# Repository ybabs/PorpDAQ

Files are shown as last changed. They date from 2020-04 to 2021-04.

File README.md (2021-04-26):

# PorpDAQ
STM32 Based design data acquisition recorder for harbour porpoises. The system is based on a 40dB bandpass preamplifier (90Khz - 150kHz). Records WAV file at a sampling rate of 400 KHz (V1) and 500 KHz (V2) and stores them to a microSD card. The preamplifier was designed using TI's filter designer tool. Preamp output is passed to a summing amplifier to keep signals within 0 - 3.3V with a 1.65V bias. There's a few iterations of the DAQ from the initial prototypes to improved designs. 

PorpDAQ has been designed to fit within a small multirotor UAV so current design weighs only 18g. PorpDAQ computes a 1024 point RFFT of incoming hydrophone signals and transmits signals within 90 - 150KHz over a UART Interface

## Rev 1 Board                         

The initial version of the DAQ was based on a STM32F746 chip and had a 400 KHz sample rate and a 12-bit ADC with a SD card write speed of about 20mbps. 

<p align="left">
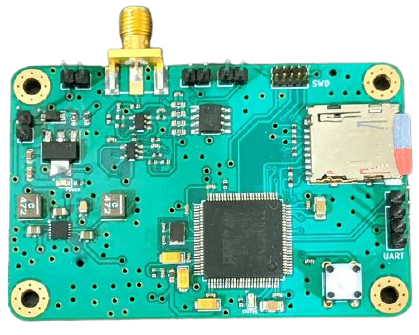
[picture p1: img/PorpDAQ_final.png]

</p>

## Rev 2 Board

Rev 2 board comes with some improvements namely the the use of the STM32H743 chip, USB-C for power with the addition of a full speed interface. 500 KHz sample rate, SD Card write speed of ~35 Mbps with a 16-bit ADC and better SNR. Also slightly smaller footprint 
<br />
<p align="left">
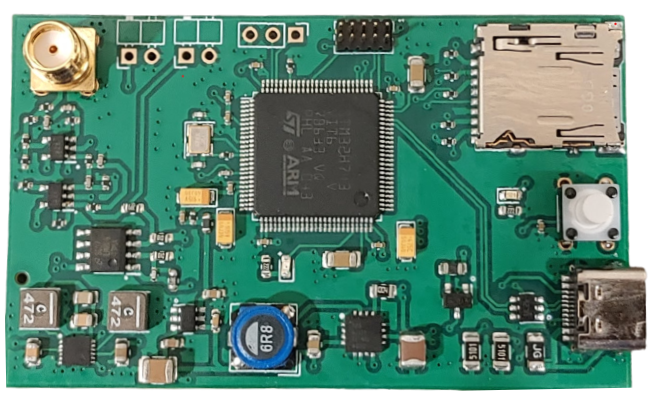
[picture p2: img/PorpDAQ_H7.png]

</p>

This repository mostly contains :
   - Hardware designs for the both revisions (circuits were simulated in MultiSim and designs were made in UltiBoard and Kicad)
   - Designs for the  different prototypes used.
   - A CM4-based design to integrate PorpDaq with a Pi4 Compute Module (WIP)
   - 3D designed case for the Rev 1 board 
   - Low level drivers and firmware (bare-metal version and FreeRTOS version for Rev1 and FreeRTOS version for Rev2)

## Note Rev2.1 now included as well.
  - 3.3V regulator on Rev 2 used a switcher and wasn't running in low noise mode (oops!) so 2.1 now uses a low noise ADP7156 3.3V regulator

## Structure
 - Firmware: Contains Custom Board FreeRTOS firmware and STM32F7 discovery board FreeRTOS and bare-metal firmware. Also contains H747 Disco Board firmware.  Please note bare-metal firmware currently has a UART TX bug preventing data from being transmmitted over the UART line.
 - Hardware: contains various designs and schematics for the board designs. **Rev 1** design is named `board_100pin` while  **Rev 2** design is named `h7_board`. 

 ## Citation (Bibtex)

` @article{Babatunde2020,
  doi = {10.3390/s20216064},
  url = {https://doi.org/10.3390/s20216064},
  year = {2020},
  month = oct,
  publisher = {{MDPI} {AG}},
  volume = {20},
  number = {21},
  pages = {6064},
  author = {Daniel Babatunde and Simon Pomeroy and Paul Lepper and Ben Clark and Rebecca Walker},
  title = {Autonomous Deployment of Underwater Acoustic Monitoring Devices Using an Unmanned Aerial Vehicle: The Flying Hydrophone},
  journal = {Sensors}
}`

## License
  MIT License Copyright 2020 Daniel Babatunde

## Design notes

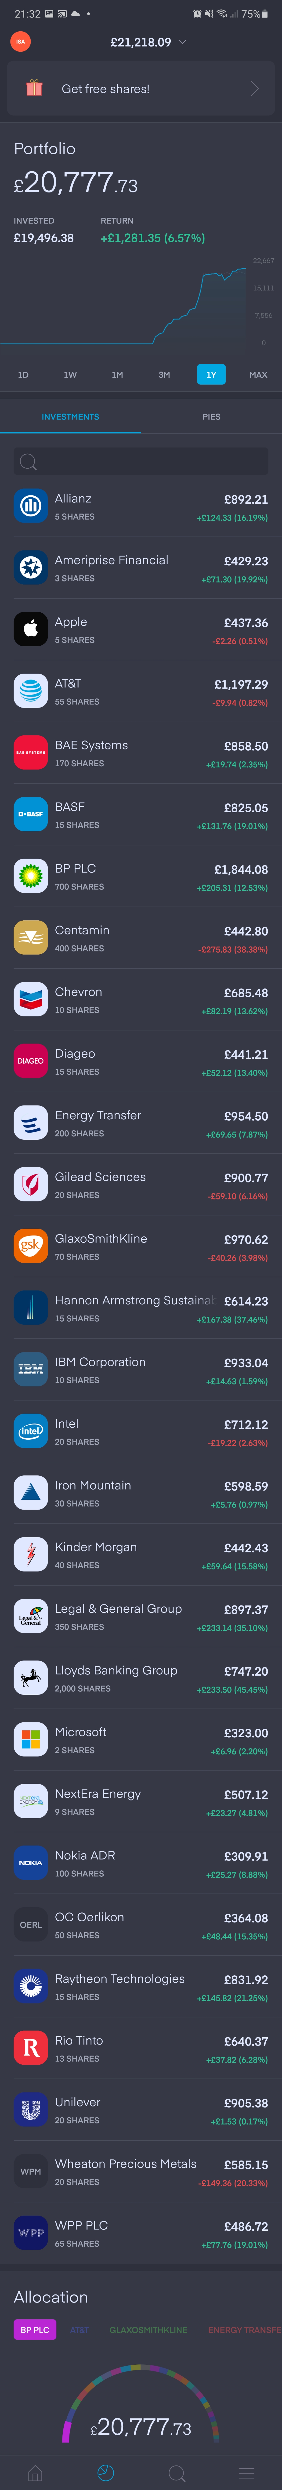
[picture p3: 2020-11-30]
Hardware/h7_lownoise/datasheets/dvi39qfev1261.jpg

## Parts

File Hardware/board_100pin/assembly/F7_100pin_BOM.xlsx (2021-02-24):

Ref | Qnty | Value | Cmp name | Footprint | Description | Manufacturer | Part Number
C2, C1, | 2 | 2.2u | C_Small | Capacitor_SMD:C_1206_3216Metric | Unpolarized capacitor, small symbol | Yageo | CC1206KKX7R7BB225 | https://www.digikey.co.uk/product-detail/en/yageo/CC1206KKX7R7BB225/311-1957-1-ND/5195859 | 0.096 | 0.192
C6, C4, C5, C3, | 4 | 100p | C_Small | Capacitor_SMD:C_0402_1005Metric | Unpolarized capacitor, small symbol | Yageo | CC0402JRNPO9BN101 | https://www.digikey.co.uk/product-detail/en/yageo/CC0402JRNPO9BN101/311-1024-1-ND/302941 | 0.0062 | 0.0248
C7, C8, | 2 | 4.3p | C_Small | Capacitor_SMD:C_0402_1005Metric | Unpolarized capacitor, small symbol | Murata | GJM1555C1H4R3BB01D | https://www.digikey.co.uk/product-detail/en/murata-electronics/GJM1555C1H4R3BB01D/490-8582-6-ND/4380999 | 0.048 | 0.096
C9, | 1 | 10p | C_Small | Capacitor_SMD:C_0402_1005Metric | Unpolarized capacitor, small symbol | Yageo | CC0402DRNPO9BN100 | https://www.digikey.co.uk/product-detail/en/yageo/CC0402DRNPO9BN100/311-3651-1-ND/8024740 | 0.0085 | 0.0085
C10, C11, | 2 | 10u | C_Small | Capacitor_SMD:C_0603_1608Metric | Unpolarized capacitor, small symbol | Murata | GRM188R61A106KE69J | https://www.digikey.co.uk/product-detail/en/murata-electronics/GRM188R61A106KE69J/490-14372-2-ND/6606001 | 0.01914 | 0.03828
C12, C13, C15, | 3 | 10u | C_Small | Capacitor_SMD:C_0805_2012Metric | Unpolarized capacitor, small symbol | Murata | GRM21BR71A106KE51 |  | 0.10981 | 0.32943
C14, | 1 | 100n | C_Small | Capacitor_SMD:C_0805_2012Metric | Unpolarized capacitor, small symbol | Murata | GRM21BR71E104KA01 |  | 0.02461 | 0.02461
C16, | 1 | 4.7u | CP_Small | Capacitor_Tantalum_SMD:CP_EIA-3216-18_Kemet-A | Polarized capacitor, small symbol | KEMET | T491A475K016AT | https://www.digikey.co.uk/product-detail/en/kemet/T491A475K016AT/399-3697-1-ND/819022 | 0.1487 | 0.1487
C24, C22, | 2 | 1u | CP_Small | Capacitor_Tantalum_SMD:CP_EIA-3216-18_Kemet-A | Polarized capacitor, small symbol | KEMET | T491A105K016AT | https://www.digikey.co.uk/product-detail/en/kemet/T491A105K016AT/399-3678-1-ND/819003 | 0.1218 | 0.2436
C26, C25, C23, C17, C18, C19, C20, C21, | 8 | 100n | C_Small | Capacitor_SMD:C_0402_1005Metric | Unpolarized capacitor, small symbol | Yageo | CC0402ZRY5V7BB104 | https://www.digikey.co.uk/product-detail/en/yageo/CC0402ZRY5V7BB104/311-1047-6-ND/578899 | 0.048 | 0.384
D1, | 1 | B5819W | D_Schottky_Small | Diode_SMD:D_SOD-123 | Schottky diode, small symbol | Micro-Commercial | B5819W-TP | https://www.digikey.co.uk/product-detail/en/micro-commercial-co/B5819W-TP/B5819W-TPMSCT-ND/10054438 | 0.103 | 0.103
D2, | 1 | Red_LED | LED_Small | LED_SMD:LED_0603_1608Metric | Light emitting diode, small symbol | Everlight | 19-217/R6C-AL1M2VY/3T | https://www.digikey.co.uk/product-detail/en/everlight-electronics-co-ltd/19-217-R6C-AL1M2VY-3T/1080-1585-6-ND/8535337 | 0.055 | 0.055
D4, | 1 | Green_LED | LED_Small | LED_SMD:LED_0603_1608Metric | Light emitting diode, small symbol | Everlight | 19-217/BHC-ZL1M2RY/3T | https://www.digikey.co.uk/products/en?keywords=19-217%2FBHC-ZL1M2RY%2F3T | 0.055 | 0.055
F1, | 1 | 500mA | Fuse_Small | Fuse:Fuse_0603_1608Metric | Fuse, small symbol | Panasonic | ERB-RE0R50V | https://www.digikey.co.uk/product-detail/en/panasonic-electronic-components/ERB-RE0R50V/P15127CT-ND/2796814 | 0.1503 | 0.1503
FB1, | 1 | 100 @ 100 MHz | Ferrite_Bead_Small | Inductor_SMD:L_0603_1608Metric | Ferrite bead, small symbol | TDK | MPZ1608S101ATAH0 | https://www.digikey.co.uk/product-detail/en/tdk-corporation/MPZ1608S101ATAH0/445-1564-1-ND/571894 | 0.0314 | 0.0314
FB2, | 1 | 100 @ 100 Mhz | Ferrite_Bead_Small | Inductor_SMD:L_0603_1608Metric | Ferrite bead, small symbol | TDK | MPZ1608S101ATAH0 | https://www.digikey.co.uk/product-detail/en/tdk-corporation/MPZ1608S101ATAH0/445-1564-1-ND/571894 | 0.0314 | 0.0314
H1, | 1 | M_HolePad | MountingHole_Pad | MountingHole:MountingHole_3.2mm_M3_Pad_Via | Mounting Hole with connection |  |  |  |  | 0
H2, H3, H4, | 3 | MHole_Pad | MountingHole_Pad | MountingHole:MountingHole_3.2mm_M3_Pad_Via | Mounting Hole with connection |  |  |  |  | 0
IC2, IC1, | 2 | OPA659IDBVR | OPA659IDBVR | SamacSys_Parts:SOT95P280X145-5N | Wideband, Unity-Gain Stable, JFET-Input OPERATIONAL AMPLIFIER | TI | OPA659IDBVR-ND | https://www.digikey.co.uk/products/en?keywords=OPA659IDBVR | 3.9404 | 7.8808
IC3, | 1 | LMH6643MAX_NOPB | LMH6643MAX_NOPB | SamacSys_Parts:SOIC127P600X175-8N | Dual Channel, Low Power, 130MHz, 75mA Rail-to-Rail Output Amplifier | TI | LMH6643MAX/NOPB | https://www.digikey.co.uk/product-detail/en/texas-instruments/LMH6643MAX-NOPB/LMH6643MAX-NOPBCT-ND/3527065 | 0.9222 | 0.9222
IC4, | 1 | TPS65133DPDR | TPS65133DPDR | SamacSys_Parts:SON45P300X300X80-13N-D | Split-Rail Converter, +/-5V, 250mA Dual Output Power Supply | TI | TPS65133DPDR | https://www.digikey.co.uk/product-detail/en/texas-instruments/TPS65133DPDR/296-40874-1-ND/5178751 | 1.2979 | 1.2979
J1, | 1 | SMA Edge | 142-0701-851 | SamacSys_Parts:142-0701-851 | SMA 50 Ohm End Launch Jack Receptacle - Tab Contact | Cinch | 142-0701-851 | https://www.digikey.co.uk/product-detail/en/cinch-connectivity-solutions-johnson/142-0701-851/J658-ND/273369 | 2.5417 | 2.5417
J2, | 1 | Pre-Amp | Conn_01x02 | Connector_PinHeader_2.54mm:PinHeader_1x02_P2.54mm_Vertical | Generic connector, single row, 01x02, script generated (kicad-library-utils/schlib/autogen/connector/) |  |  |  |  | 0
J3, | 1 | UART | Conn_01x04 | Connector_PinHeader_2.54mm:PinHeader_1x04_P2.54mm_Vertical | Generic connector, single row, 01x04, script generated (kicad-library-utils/schlib/autogen/connector/) |  |  |  |  | 0
J4, | 1 | 5V | Conn_01x02 | Connector_PinHeader_2.54mm:PinHeader_1x02_P2.54mm_Vertical | Generic connector, single row, 01x02, script generated (kicad-library-utils/schlib/autogen/connector/) |  |  |  |  | 0
J5, | 1 | Filter | Conn_01x02 | Connector_PinHeader_2.54mm:PinHeader_1x02_P2.54mm_Vertical | Generic connector, single row, 01x02, script generated (kicad-library-utils/schlib/autogen/connector/) |  |  |  |  | 0
J6, | 1 | 3V3 | Conn_01x02 | Connector_PinHeader_2.54mm:PinHeader_1x02_P2.54mm_Vertical | Generic connector, single row, 01x02, script generated (kicad-library-utils/schlib/autogen/connector/) |  |  |  |  | 0
J7, | 1 | SWDIO | Conn_02x05_Odd_Even | Connector_PinHeader_1.27mm:PinHeader_2x05_P1.27mm_Vertical | Generic connector, double row, 02x05, odd/even pin numbering scheme (row 1 odd numbers, row 2 even numbers), script generated (kicad-library-utils/schlib/autogen/connector/) |  |  | https://www.digikey.co.uk/product-detail/en/sullins-connector-solutions/GRPB052VWVN-RC/S9015E-05-ND/1786455 | 0.4017 | 0.4017
J8, | 1 | Micro_SD_Card | Micro_SD_Card | Connector_Card:microSD_HC_Hirose_DM3AT-SF-PEJM5 | Micro SD Card Socket | HiROse | DM3AT-SF-PEJM5 | https://www.digikey.co.uk/product-detail/en/hirose-electric-co-ltd/DM3AT-SF-PEJM5/HR1964CT-ND/2533566 | 1.4646 | 1.4646
L1, L2, | 2 | 4.7u | L | Inductor_SMD:L_Coilcraft_XxL4020 | Inductor | Coilmaster | MMPP252012-4R7N |  | 0.68908 | 1.37816
R1, | 1 | 44.2k | R_Small_US | Resistor_SMD:R_0402_1005Metric | Resistor, small US symbol | TE | CPF0402B44K2E1 | https://www.digikey.co.uk/product-detail/en/te-connectivity-passive-product/CPF0402B44K2E1/A102862CT-ND/2729395 | 0.1777 | 0.1777
R2, | 1 | 66.5k | R_Small_US | Resistor_SMD:R_0402_1005Metric | Resistor, small US symbol | Yageo | RT0402BRD0766K5L | https://www.digikey.co.uk/product-detail/en/yageo/RT0402BRD0766K5L/YAG4298CT-ND/6616454 | 0.0915 | 0.0915
R3, | 1 | 35.7k | R_Small_US | Resistor_SMD:R_0402_1005Metric | Resistor, small US symbol | StackPole | RMCF0402FT35K7 | https://www.digikey.co.uk/product-detail/en/stackpole-electronics-inc/RMCF0402FT35K7/RMCF0402FT35K7CT-ND/2417653 | 0.0039 | 0.0039
R4, | 1 | 34.8k | R_Small_US | Resistor_SMD:R_0402_1005Metric | Resistor, small US symbol | Yageo | RC0402FR-0734K8L | https://www.digikey.co.uk/product-detail/en/yageo/RC0402FR-0734K8L/YAG3125TR-ND/5280985 | 0.0042 | 0.0042
R5, | 1 | 6.34k | R_Small_US | Resistor_SMD:R_0402_1005Metric | Resistor, small US symbol | Panasonic | ERA-2AEB6341X | https://www.digikey.co.uk/product-detail/en/panasonic-electronic-components/ERA-2AEB6341X/P6-34KDCCT-ND/3063872 | 0.0814 | 0.0814
R6, R13, | 2 | 10k | R_Small_US | Resistor_SMD:R_0402_1005Metric | Resistor, small US symbol | Yageo | RC0100JR-0710KL | https://www.digikey.co.uk/product-detail/en/yageo/RC0100JR-0710KL/311-10KDHCT-ND/2254412 | 0.0323 | 0.0646
R9, R7, | 2 | 187 | R_Small_US | Resistor_SMD:R_0402_1005Metric | Resistor, small US symbol | Yageo | AC0402FR-07187RL | https://www.mouser.co.uk/ProductDetail/Yageo/AC0402FR-07187RL?qs=sGAEpiMZZMvdGkrng054t7zOzNqIRvGcfoVYBvhPxz4%3D | 0.005 | 0.01
R10, R8, | 2 | 2.49k | R_Small_US | Resistor_SMD:R_0402_1005Metric | Resistor, small US symbol | Panasonic | ERA-2AEB2491X | https://www.digikey.co.uk/product-detail/en/panasonic-electronic-components/ERA-2AEB2491X/P2-49KDCCT-ND/3063743 | 0.0814 | 0.1628
R15, R11, | 2 | 50k | R_Small_US | Resistor_SMD:R_0603_1608Metric | Resistor, small US symbol | StackPole | RMCF0201FT49K9 | https://www.digikey.co.uk/product-detail/en/stackpole-electronics-inc/RMCF0201FT49K9/RMCF0201FT49K9CT-ND/3931518 | 0.0069 | 0.0138
R16, R14, | 2 | 100k | R_Small_US | Resistor_SMD:R_0603_1608Metric | Resistor, small US symbol | Yageo | RC0402FR-07100KL | https://www.digikey.co.uk/product-detail/en/yageo/RC0402FR-07100KL/311-100KLRCT-ND/729473 | 0.0042 | 0.0084
R20, R21, R22, R23, R19, | 5 | 47k | R_Small_US | Resistor_SMD:R_0402_1005Metric | Resistor, small US symbol | Yageo | RC0201FR-07100KL | https://www.digikey.co.uk/product-detail/en/panasonic-electronic-components/ERA-2AEB473X/P47KDCCT-ND/1706223 | 0.0814 | 0.407
R24, R12, | 2 | 2k2 | R_Small_US | Resistor_SMD:R_0402_1005Metric | Resistor, small US symbol | TE | CRGP0402F2K2 | https://www.digikey.co.uk/product-detail/en/te-connectivity-passive-product/CRGP0402F2K2/A130359CT-ND/8578191 | 0.0237 | 0.0474
R25, | 1 | 0 | R_Small_US | Resistor_SMD:R_0402_1005Metric | Resistor, small US symbol | Yageo | RC0402JR-070RL | https://www.digikey.co.uk/product-detail/en/yageo/RC0402JR-070RL/311-0-0JRDKR-ND/732300 | 0.0034 | 0.0034
S1, | 1 | TL1105CF160Q | TL1105CF160Q | SamacSys_Parts:TL1105CF160Q | Tactile Switches 6X6X8MM 160GF | E-Switch | TL1105CF160Q | https://www.digikey.co.uk/products/en?keywords=TL1105CF160Q | 0.1227 | 0.1227
U1, | 1 | AMS1117-3.3 | AMS1117-3.3 | Package_TO_SOT_SMD:SOT-223-3_TabPin2 | 1A Low Dropout regulator, positive, 3.3V fixed output, SOT-223 | Advanced Monolithic Systems | AMS1117-3.3 |  | 1.29 | 1.29
U2, | 1 | STM32F746VGTx | STM32F746VGTx | Package_QFP:LQFP-100_14x14mm_P0.5mm | ARM Cortex-M7 MCU, 1024KB flash, 320KB RAM, 216MHz, 1.7-3.6V, 82 GPIO, LQFP-100 | STMicroelectronics | STM32F746VGT7 | https://www.digikey.co.uk/product-detail/en/stmicroelectronics/STM32F746VGT7/497-STM32F746VGT7-ND/6207502 | 8.90963 | 8.90963
X1, | 1 | NX3325GD | Crystal | SamacSys_Parts:RESC3226X100N | Two pin crystal | NDK | NX3225GD-8MHz-EXS00A-CG04874 | https://www.digikey.co.uk/product-detail/en/ndk-america-inc/NX3225GD-8MHZ-EXS00A-CG04874/644-1391-1-ND/9172119 | 0.3757 | 0.3757
 |  |  |  |  |  |  |  |  |  | 29.57721
 |  |  |  |  |  |  |  |  |  | 5.48

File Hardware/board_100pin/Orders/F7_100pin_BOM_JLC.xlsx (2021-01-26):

Designator | Quantity | Value | Footprint | LCSC Part #
C2, C1, | 2 | 2.2u | 1206 | C50254
C6, C4, C5, C3, | 4 | 100p | 402 | C1546 (https://lcsc.com/product-detail/Multilayer-Ceramic-Capacitors-MLCC-SMD-SMT_100pF-101-5-50V_C1546.html/?href=jlc-SMT)
C7, C8, | 2 | 4.3p | 402 | C159803 (https://lcsc.com/product-detail/Multilayer-Ceramic-Capacitors-MLCC-SMD-SMT_SAMSUNG_CL05C4R3CB5NNNC_4-3pF-4R3-0-25pF-50V_C159803.html/?href=jlc-SMT)
C9, | 1 | 10p | 402 | C32949 (https://lcsc.com/product-detail/Multilayer-Ceramic-Capacitors-MLCC-SMD-SMT_SAMSUNG_CL05C100JB5NNNC_10pF-100-5-50V_C32949.html/?href=jlc-SMT)
C10, C11, | 2 | 10u | 603 | C19702
C12, C13, C15, | 3 | 10u | 805
C14, | 1 | 100n | 805
C16, | 1 | 4.7u | EIA-3216-18 | C7187 (https://lcsc.com/product-detail/Tantalum-Capacitors_AVX_TAJA475K016RNJ_4-7uF-475-10-16V_C7187.html/?href=jlc-SMT)
C24, C22, | 2 | 1u | EIA-3216-18 | C7176
C26, C25, C23, C17, C18, C19, C20, C21, | 8 | 100n | 402 | C1525 (https://lcsc.com/product-detail/Multilayer-Ceramic-Capacitors-MLCC-SMD-SMT_SAMSUNG_CL05B104KO5NNNC_100nF-104-10-16V_C1525.html/?href=jlc-SMT)
D1, | 1 | B5819W | SOD-123 | C8598
D2, | 1 | Red_LED | 603 | C2286
D4, | 1 | Green_LED | 603 | C72043
F1, | 1 | 500mA | 603
FB1, | 1 | 100 @ 100 MHz | 603
FB2, | 1 | 100 @ 100 Mhz | 603
IC2, IC1, | 2 | OPA659IDBVR | SOT-23
IC3, | 1 | LMH6643MAX_NOPB | SOIC-8
IC4, | 1 | TPS65133DPDR | 12-WSON | C134100
J1, | 1 | SMA Edge
J2, | 1 | Pre-Amp | Connector_PinHeader_2.54mm:PinHeader_1x02_P2.54mm_Vertical
J3, | 1 | UART | Connector_PinHeader_2.54mm:PinHeader_1x04_P2.54mm_Vertical
J4, | 1 | USB_B_Micro | USB_B_Micro
J5, | 1 | Filter | Connector_PinHeader_2.54mm:PinHeader_1x02_P2.54mm_Vertical
J6, | 1 | 3V3 | Connector_PinHeader_2.54mm:PinHeader_1x02_P2.54mm_Vertical
J7, | 1 | SWDIO | Connector_PinHeader_1.27mm:PinHeader_2x05_P1.27mm_Vertical
J8, | 1 | Micro_SD_Card | Connector_Card:microSD_HC_Hirose_DM3AT-SF-PEJM5 | C114218
L1, L2, | 2 | 4.7u | Inductor_SMD:L_Coilcraft_XxL4020
R1, | 1 | 44.2k | 402 | C25895 (https://lcsc.com/product-detail/Chip-Resistor-Surface-Mount_Uniroyal-Elec-0402WGF4422TCE_C25895.html/?href=jlc-SMT)
R2, | 1 | 66.5k | 402 | C29381 (https://lcsc.com/product-detail/Chip-Resistor-Surface-Mount_Uniroyal-Elec-0402WGF6652TCE_C29381.html/?href=jlc-SMT)
R3, | 1 | 35.7k | 402 | C26975 (https://lcsc.com/product-detail/Chip-Resistor-Surface-Mount_Uniroyal-Elec-0402WGF3572TCE_C26975.html/?href=jlc-SMT)
R4, | 1 | 34.8k | 402 | C47493 (https://lcsc.com/product-detail/Chip-Resistor-Surface-Mount_Uniroyal-Elec-0402WGF3482TCE_C47493.html/?href=jlc-SMT)
R5, | 1 | 6.34k | 402 | C45013 (https://lcsc.com/product-detail/Chip-Resistor-Surface-Mount_Uniroyal-Elec-0402WGF6341TCE_C45013.html/?href=jlc-SMT)
R6, R13, | 2 | 10k | 402 | C25744
R9, R7, | 2 | 187 | 402 | C39887 (https://lcsc.com/product-detail/Chip-Resistor-Surface-Mount_Uniroyal-Elec-0402WGF1870TCE_C39887.html/?href=jlc-SMT)
R10, R8, | 2 | 2.49k | 402 | C25884 (https://lcsc.com/product-detail/Chip-Resistor-Surface-Mount_Uniroyal-Elec-0402WGF2491TCE_C25884.html/?href=jlc-SMT)
R15, R11, | 2 | 50k | 603 | C23184 (https://lcsc.com/product-detail/Chip-Resistor-Surface-Mount_Uniroyal-Elec-0603WAF4992T5E_C23184.html/?href=jlc-SMT)
R16, R14, | 2 | 100k | 603 | C25803 (https://lcsc.com/product-detail/Chip-Resistor-Surface-Mount_Uniroyal-Elec-0603WAF1003T5E_C25803.html/?href=jlc-SMT)
R20, R21, R22, R23, R19, | 5 | 47k | 402 | C25792 (https://lcsc.com/product-detail/Chip-Resistor-Surface-Mount_Uniroyal-Elec-0402WGF4702TCE_C25792.html/?href=jlc-SMT)
R24, R12, | 2 | 2k2 | 402 | C25879 (https://lcsc.com/product-detail/Chip-Resistor-Surface-Mount_Uniroyal-Elec-0402WGF2201TCE_C25879.html/?href=jlc-SMT)
R25, | 1 | 0 | 402 | C17168 (https://lcsc.com/product-detail/Chip-Resistor-Surface-Mount_Uniroyal-Elec-0402WGF0000TCE_C17168.html/?href=jlc-SMT)
S1, | 1 | TL1105CF160Q | SamacSys_Parts:TL1105CF160Q | C273468
U1, | 1 | AMS1117-3.3 | SOT223-3 | C6186
U2, | 1 | STM32F746VGTx | LQFP-100_14.0x14.0x0.5P | C87664 (https://lcsc.com/product-detail/ST-Microelectronics_STMicroelectronics_STM32F746VGT6_STM32F746VGT6_C87664.html/?href=jlc-SMT)
X1, | 1 | NX3325GD | SamacSys_Parts:RESC3226X100N

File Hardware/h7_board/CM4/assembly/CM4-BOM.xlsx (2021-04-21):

Comment | Designator | Footprint | LCSC
10u | C1,C2,C28 | Capacitor_SMD:C_0603_1608Metric | C19702
100p | C10,C11,C12,C30,C31 | Capacitor_SMD:C_0402_1005Metric | C1546
4.7u | C13 | Capacitor_Tantalum_SMD:CP_EIA-3216-18_Kemet-A | C7187
2.2u | C15,C19 | Capacitor_SMD:C_1206_3216Metric | C50254
100n X7R | C22 | Capacitor_SMD:C_0603_1608Metric | C14663
1u | C23,C25 | Capacitor_Tantalum_SMD:CP_EIA-3216-18_Kemet-A | C7176
47p | C29 | Capacitor_SMD:C_0402_1005Metric | C1567
1u | C3,C4,C5,C27 | Capacitor_SMD:C_0603_1608Metric | C15849
10u | C32 | Capacitor_Tantalum_SMD:CP_EIA-3216-18_Kemet-A | C7171
100n | C14,C16,C17,C18,C20,C21,C24,C26,C33,C34,C50 | Capacitor_SMD:C_0402_1005Metric | C1525
12p | C48,C49 | Capacitor_SMD:C_0402_1005Metric | C1547
10u | C6,C7,C9 | Capacitor_SMD:C_0805_2012Metric | C15850
100n | C8 | Capacitor_SMD:C_0805_2012Metric | C49678
LED_Red | D2 | LED_SMD:LED_0603_1608Metric | C2286
LED | D3 | LED_SMD:LED_0603_1608Metric | C72043
Polyfuse | F1 | Fuse:Fuse_1206_3216Metric | C369159
600 @ 100MHz | FB1 | Inductor_SMD:L_0805_2012Metric | C1017
100 @ 100 MHz | FB2 | Inductor_SMD:L_0603_1608Metric | C74325
Fiducial | FID1,FID2,FID3 | Fiducial:Fiducial_0.5mm_Mask1.5mm
ADP7156ARDZ-3.3-R7 | IC1 | SamacSys_Parts:SOIC127P600X175-9N
OPA659IDBVR | IC2,IC3 | SamacSys_Parts:SOT95P280X145-5N
TPS65133DPDR | IC4 | SamacSys_Parts:SON45P300X300X80-13N-D | C134100
OPA377AIDCKR | IC5 | SamacSys_Parts:SOT65P210X110-5N
USB_C_Receptacle_USB2.0 | J1 | CM4IO:TYPE-C-31-M-12 | C165948
Conn_Coaxial | J2 | Connector_Coaxial:SMA_Wurth_60312002114503_Vertical
SWDIO | J3 | Connector_PinHeader_1.27mm:PinHeader_2x05_P1.27mm_Vertical
Micro_SD_Card | J4 | Connector_Card:microSD_HC_Hirose_DM3AT-SF-PEJM5
USART | J7 | Connector_PinHeader_2.54mm:PinHeader_1x03_P2.54mm_Vertical
4.7u | L1,L2 | Inductor_SMD:L_Coilcraft_XxL4020
AO3401A | Q1 | SamacSys_Parts:SOT95P280X125-3N | C15127
5.1k | R1,R2 | Resistor_SMD:R_1206_3216Metric | C26033
2.49k | R10,R12 | Resistor_SMD:R_0402_1005Metric | C25884
50k | R13 | Resistor_SMD:R_0603_1608Metric | C23184
100k | R14,R16 | Resistor_SMD:R_0603_1608Metric | C25803
49.9k | R15 | Resistor_SMD:R_0603_1608Metric | C23184
47k | R17,R19,R22,R23,R24 | Resistor_SMD:R_0402_1005Metric | C25792
0 | R18 | Resistor_SMD:R_0402_1005Metric | C17168
47 | R20 | Resistor_SMD:R_0402_1005Metric | C25118
2k2 | R21 | Resistor_SMD:R_0603_1608Metric | C4190
2.2k | R28 | Resistor_SMD:R_0603_1608Metric | C4190
44.2k | R3 | Resistor_SMD:R_0402_1005Metric | C25895
66.5k | R4 | Resistor_SMD:R_0402_1005Metric | C29381
6.34k | R5 | Resistor_SMD:R_0402_1005Metric | C45013
35.7k | R6 | Resistor_SMD:R_0402_1005Metric | C26975
34.8k | R7 | Resistor_SMD:R_0402_1005Metric | C47493
10k | R8,R27 | Resistor_SMD:R_0402_1005Metric | C25744
187 | R9,R11 | Resistor_SMD:R_0402_1005Metric | C39887
TL1105CF160Q | S1 | SamacSys_Parts:TL1105CF160Q
STM32H743VITx | U2 | Package_QFP:LQFP-100_14x14mm_P0.5mm
REF3433IDBVR | U3 | REF3433:REF3433IDBVR
USBLC6-2SC6 | U4 | Package_TO_SOT_SMD:SOT-23-6 | C7519
16MHz | Y1 | Crystal:Crystal_SMD_3225-4Pin_3.2x2.5mm | C13738

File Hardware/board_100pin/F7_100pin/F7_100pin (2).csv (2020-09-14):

Source: | C:\Users\Home\OneDrive\PhD\Phocoena-DAQ\Hardware\board_100pin\F7_100pin\F7_100pin.sch
Date: | 14/09/2020 15:16:51
Tool: | Eeschema (5.1.4)-1
Generator: | C:\Program Files\KiCad\bin\scripting\plugins/bom_csv_grouped_by_value_with_fp.py
Component Count: | 77
Ref | Qnty | Value | Cmp name | Footprint | Description | Vendor
C2, C1, | 2 | 2.2u | C_Small | Capacitor_SMD:C_1206_3216Metric | Unpolarized capacitor, small symbol
C6, C4, C5, C3, | 4 | 100p | C_Small | Capacitor_SMD:C_0402_1005Metric | Unpolarized capacitor, small symbol
C7, C8, | 2 | 4.3p | C_Small | Capacitor_SMD:C_0402_1005Metric | Unpolarized capacitor, small symbol
C9, | 1 | 10p | C_Small | Capacitor_SMD:C_0402_1005Metric | Unpolarized capacitor, small symbol
C10, C11, | 2 | 10u | C_Small | Capacitor_SMD:C_0603_1608Metric | Unpolarized capacitor, small symbol
C12, C13, C15, | 3 | 10u | C_Small | Capacitor_SMD:C_0805_2012Metric | Unpolarized capacitor, small symbol
C14, | 1 | 100n | C_Small | Capacitor_SMD:C_0805_2012Metric | Unpolarized capacitor, small symbol
C16, | 1 | 4.7u | CP_Small | Capacitor_Tantalum_SMD:CP_EIA-3216-18_Kemet-A | Polarized capacitor, small symbol
C24, C22, | 2 | 1u | CP_Small | Capacitor_Tantalum_SMD:CP_EIA-3216-18_Kemet-A | Polarized capacitor, small symbol
C25, C23, C17, C18, C19, C20, C21, C26, | 8 | 100n | C_Small | Capacitor_SMD:C_0402_1005Metric | Unpolarized capacitor, small symbol
D1, | 1 | B5819W | D_Schottky_Small | Diode_SMD:D_SOD-123 | Schottky diode, small symbol
D2, | 1 | Red_LED | LED_Small | LED_SMD:LED_0603_1608Metric | Light emitting diode, small symbol
D4, | 1 | Green_LED | LED_Small | LED_SMD:LED_0603_1608Metric | Light emitting diode, small symbol
F1, | 1 | 500mA | Fuse_Small | Fuse:Fuse_0603_1608Metric | Fuse, small symbol
FB1, | 1 | 100 @ 100 MHz | Ferrite_Bead_Small | Inductor_SMD:L_0603_1608Metric | Ferrite bead, small symbol
FB2, | 1 | 100 @ 100 Mhz | Ferrite_Bead_Small | Inductor_SMD:L_0603_1608Metric | Ferrite bead, small symbol
H1, | 1 | M_HolePad | MountingHole_Pad | MountingHole:MountingHole_3.2mm_M3_Pad_Via | Mounting Hole with connection
H2, H3, H4, | 3 | MHole_Pad | MountingHole_Pad | MountingHole:MountingHole_3.2mm_M3_Pad_Via | Mounting Hole with connection
IC2, IC1, | 2 | OPA659IDBVR | OPA659IDBVR | SamacSys_Parts:SOT95P280X145-5N | Wideband, Unity-Gain Stable, JFET-Input OPERATIONAL AMPLIFIER
IC3, | 1 | LMH6643MAX_NOPB | LMH6643MAX_NOPB | SamacSys_Parts:SOIC127P600X175-8N | Dual Channel, Low Power, 130MHz, 75mA Rail-to-Rail Output Amplifier
IC4, | 1 | TPS65133DPDR | TPS65133DPDR | SamacSys_Parts:SON45P300X300X80-13N-D | Split-Rail Converter, +/-5V, 250mA Dual Output Power Supply
J1, | 1 | SMA Edge | 142-0701-851 | SamacSys_Parts:142-0701-851 | SMA 50 Ohm End Launch Jack Receptacle - Tab Contact
J2, | 1 | Pre-Amp | Conn_01x02 | Connector_PinHeader_2.54mm:PinHeader_1x02_P2.54mm_Vertical | Generic connector, single row, 01x02, script generated (kicad-library-utils/schlib/autogen/connector/)
J3, | 1 | UART | Conn_01x04 | Connector_PinHeader_2.54mm:PinHeader_1x04_P2.54mm_Vertical | Generic connector, single row, 01x04, script generated (kicad-library-utils/schlib/autogen/connector/)
J4, | 1 | USB_B_Micro | USB_B_Micro | Connector_USB:USB_Micro-B_GCT_USB3076-30-A | USB Micro Type B connector
J5, | 1 | Filter | Conn_01x02 | Connector_PinHeader_2.54mm:PinHeader_1x02_P2.54mm_Vertical | Generic connector, single row, 01x02, script generated (kicad-library-utils/schlib/autogen/connector/)
J6, | 1 | 3V3 | Conn_01x02 | Connector_PinHeader_2.54mm:PinHeader_1x02_P2.54mm_Vertical | Generic connector, single row, 01x02, script generated (kicad-library-utils/schlib/autogen/connector/)
J7, | 1 | SWDIO | Conn_02x05_Odd_Even | Connector_PinHeader_1.27mm:PinHeader_2x05_P1.27mm_Vertical | Generic connector, double row, 02x05, odd/even pin numbering scheme (row 1 odd numbers, row 2 even numbers), script generated (kicad-library-utils/schlib/autogen/connector/)
J8, | 1 | Micro_SD_Card | Micro_SD_Card | Connector_Card:microSD_HC_Hirose_DM3AT-SF-PEJM5 | Micro SD Card Socket
L1, L2, | 2 | 4.7u | L | Inductor_SMD:L_Coilcraft_XxL4020 | Inductor
R1, | 1 | 44.2k | R_Small_US | Resistor_SMD:R_0402_1005Metric | Resistor, small US symbol
R2, | 1 | 66.5k | R_Small_US | Resistor_SMD:R_0402_1005Metric | Resistor, small US symbol
R3, | 1 | 35.7k | R_Small_US | Resistor_SMD:R_0402_1005Metric | Resistor, small US symbol
R4, | 1 | 34.8k | R_Small_US | Resistor_SMD:R_0402_1005Metric | Resistor, small US symbol
R5, | 1 | 6.34k | R_Small_US | Resistor_SMD:R_0402_1005Metric | Resistor, small US symbol
R6, R13, | 2 | 10k | R_Small_US | Resistor_SMD:R_0402_1005Metric | Resistor, small US symbol
R9, R7, | 2 | 187 | R_Small_US | Resistor_SMD:R_0402_1005Metric | Resistor, small US symbol
R10, R8, | 2 | 2.49k | R_Small_US | Resistor_SMD:R_0402_1005Metric | Resistor, small US symbol
R15, R11, | 2 | 50k | R_Small_US | Resistor_SMD:R_0603_1608Metric | Resistor, small US symbol
R16, R14, | 2 | 100k | R_Small_US | Resistor_SMD:R_0603_1608Metric | Resistor, small US symbol
R20, R21, R22, R23, R19, | 5 | 47k | R_Small_US | Resistor_SMD:R_0402_1005Metric | Resistor, small US symbol
R24, R12, | 2 | 2k2 | R_Small_US | Resistor_SMD:R_0402_1005Metric | Resistor, small US symbol
R25, | 1 | 0 | R_Small_US | Resistor_SMD:R_0402_1005Metric | Resistor, small US symbol
S1, | 1 | TL1105CF160Q | TL1105CF160Q_0 | SamacSys_Parts:TL1105CF160Q
U1, | 1 | AMS1117-3.3 | AMS1117-3.3 | Package_TO_SOT_SMD:SOT-223-3_TabPin2 | 1A Low Dropout regulator, positive, 3.3V fixed output, SOT-223
U2, | 1 | STM32F746VGTx | STM32F746VGTx | Package_QFP:LQFP-100_14x14mm_P0.5mm | ARM Cortex-M7 MCU, 1024KB flash, 320KB RAM, 216MHz, 1.7-3.6V, 82 GPIO, LQFP-100
X1, | 1 | NX3325GD | Crystal | SamacSys_Parts:RESC3226X100N | Two pin crystal

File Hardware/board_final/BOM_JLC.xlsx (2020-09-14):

Designator | Quantity | Value | footprint | LCSC Part #
U1 | 1 | AMS1117-3.3 | SOT223-3 | C6186
FB1 | 1 | 100 @ 100 MHz | 603 | C1002
F1 | 1 | 500mA | 603 | C10677
D2 | 1 | B5819W | SOD-123 | C8598
C31 | 1 | 10u | 603 | C19702
C32 | 1 | 10u | 603 | C19702
FB2 | 1 | 100 @ 100 MHz | 603 | C1002
C36 | 1 | 1u | EIA-3216-18 | C7176
C37 | 1 | 100n | 402 | C1525
C18 | 1 | 100n | 402 | C1525
C19 | 1 | 100n | 402 | C1525
C20 | 1 | 100n | 402 | C1525
C21 | 1 | 100n | 402 | C1525
C22 | 1 | 100n | 402 | C1525
C23 | 1 | 100n | 402 | C1525
C24 | 1 | 100n | 402 | C1525
C25 | 1 | 100n | 402 | C1525
C26 | 1 | 100n | 402 | C1525
C16 | 1 | 100n | 402 | C1525
C17 | 1 | 100n | 402 | C1525
C7 | 1 | 100n | 402 | C1525
C8 | 1 | 100n | 402 | C1525
C9 | 1 | 100n | 402 | C1525
C10 | 1 | 100n | 402 | C1525
C11 | 1 | 100n | 402 | C1525
C12 | 1 | 100n | 402 | C1525
C13 | 1 | 100n | 402 | C1525
C14 | 1 | 100n | 402 | C1525
C15 | 1 | 100n | 402 | C1525
C5 | 1 | 100n | 402 | C1525
C6 | 1 | 100n | 402 | C1525
C4 | 1 | 100n | 402 | C1525
C3 | 1 | 1u | EIA-3216-18 | C7176
C2 | 1 | 4.7u | EIA-3216-18 | C161817
C1 | 1 | 4.7u | EIA-3216-18 | C161817
HSE1 | 1 | 25MHz | SMD-3225_4P | C9006
R2 | 1 | 100 | 402 | C25076
C28 | 1 | 18p | 402 | C1549
C29 | 1 | 18p | 402 | C1549
R4 | 1 | 10k | 402 | C25744
C30 | 1 | 2.2u | 1206 | C50254
C33 | 1 | 2.2u | 1206 | C50254
C34 | 1 | 1u | EIA-3216-18 | C7176
C35 | 1 | 100n | 402 | C1525
R3 | 1 | 0 | 402 | C17168
R5 | 1 | 10k | 402 | C25744
D3 | 1 | Red LED | 603 | C2286
C27 | 1 | 100n | 402 | C1525
R11 | 1 | 512 | 603 | C51224
U2 | 1 | STM32F746ZGT6 | Package_QFP:LQFP-144_20x20mm_P0.5mm | C90750
R15 | 1 | 10k | 402 | C25744
R14 | 1 | 10k | 402 | C25744
C41 | 1 | 100n | 402 | C1525
C40 | 1 | 10u | 603 | C19702
C38 | 1 | 10u | 603 | C19702
C39 | 1 | 100n | 603 | C14663
R16 | 1 | 4.99k | 402 | C25903
J6 | 1 | 142-0701-851 | SamacSys_Parts:142-0701-851
R21 | 1 | 418 | 402
R25 | 1 | 558 | 402 | C67558
R17 | 1 | 4.52k | 402
C46 | 1 | 1.3n | 603
C42 | 1 | 1.3n | 603
U3 | 1 | ADA4807-1 | SOT23-6
R22 | 1 | 406 | 402
R26 | 1 | 541 | 402
R18 | 1 | 4.39k | 402
C47 | 1 | 1.1n | 603
C43 | 1 | 1.1n | 603
U4 | 1 | ADA4807-1 | SOT-23-6
R23 | 1 | 1.02k | 402
R27 | 1 | 106 | 402
R19 | 1 | 11k | 402
C48 | 1 | 1.5n | 603
C44 | 1 | 1.5n | 603
U5 | 1 | ADA4807-1 | SOT-23-6
R24 | 1 | 966 | 402
R28 | 1 | 100 | 402
R20 | 1 | 10.4k | 402
C49 | 1 | 1n | 603 | C1588
C45 | 1 | 1n | 603 | C1588
U6 | 1 | ADA4807-1 | SOT-23-6
J5 | 1 | PJS008-2003-1 | SamacSys_Parts:PJS00820031
R13 | 1 | 0 | 402
R12 | 1 | NA | 402
R6 | 1 | 47k | 402 | C25792
R7 | 1 | 47k | 402 | C25792
R8 | 1 | 47k | 402 | C25792
R9 | 1 | 47k | 402 | C25792
R10 | 1 | 47k | 402 | C25792
IC1 | 1 | AD8031ARZ | SamacSys_Parts:SOIC127P600X175-8N
R1 | 1 | 2k2 | 603 | C4190
D1 | 1 | Green LED | 603 | C72043
S1 | 1 | TL1105CF160Q | SamacSys_Parts:TL1105CF160Q

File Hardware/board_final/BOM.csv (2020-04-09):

Designator | Quantity | Value | footprint | LCSC Part # | Farnell Part #
U1 | 1 | AMS1117-3.3 | SOT223-3 | C6186 | 3007498
FB1 | 1 | 100 @ 100 MHz | 0603
F1 | 1 | 500mA | 0603
D2 | 1 | B5819W | SOD-123
C31 | 1 | 10u | 0603 | C19702 | 1867954
C32 | 1 | 10u | 0603 | C19702 | 1867954
FB2 | 1 | 100 @ 100 MHz | 0603
C36 | 1 | 1u | EIA-3216-18 | C7176 | 145706
C37 | 1 | 100n | 0402 | C1525 | 1867948
C18 | 1 | 100n | 0402 | C1525 | 1867948
C19 | 1 | 100n | 0402 | C1525 | 1867948
C20 | 1 | 100n | 0402 | C1525 | 1867948
C21 | 1 | 100n | 0402 | C1525 | 1867948
C22 | 1 | 100n | 0402 | C1525 | 1867948
C23 | 1 | 100n | 0402 | C1525 | 1867948
C24 | 1 | 100n | 0402 | C1525 | 1867948
C25 | 1 | 100n | 0402 | C1525 | 1867948
C26 | 1 | 100n | 0402 | C1525 | 1867948
C16 | 1 | 100n | 0402 | C1525 | 1867948
C17 | 1 | 100n | 0402 | C1525 | 1867948
C7 | 1 | 100n | 0402 | C1525 | 1867948
C8 | 1 | 100n | 0402 | C1525 | 1867948
C9 | 1 | 100n | 0402 | C1525 | 1867948
C10 | 1 | 100n | 0402 | C1525 | 1867948
C11 | 1 | 100n | 0402 | C1525 | 1867948
C12 | 1 | 100n | 0402 | C1525 | 1867948
C13 | 1 | 100n | 0402 | C1525 | 1867948
C14 | 1 | 100n | 0402 | C1525 | 1867948
C15 | 1 | 100n | 0402 | C1525 | 1867948
C5 | 1 | 100n | 0402 | C1525 | 1867948
C6 | 1 | 100n | 0402 | C1525 | 1867948
C4 | 1 | 100n | 0402 | C1525 | 1867948
C3 | 1 | 1u | EIA-3216-18 | C7176 | 145706
C2 | 1 | 4.7u | EIA-3216-18 | C161817 | 1641479
C1 | 1 | 4.7u | EIA-3216-18 | C161817 | 1641479
HSE1 | 1 | 25MHz | Crystal:Crystal_SMD_3225-4Pin_3.2x2.5mm | C9006
R2 | 1 | 100 | 0402 | C25076 | 1469672
C28 | 1 | 18p | 0402 | C1549 | 1740572
C29 | 1 | 18p | 0402 | C1549 | 1740572
R4 | 1 | 10k | 0402 | C25744
C30 | 1 | 2.2u | 1206 | C50254 | 2887204
C33 | 1 | 2.2u | 1206 | C50254 | 2887204
C34 | 1 | 1u | EIA-3216-18 | C7176 | 145706
C35 | 1 | 100n | 0402 | C1525 | 1867948
R3 | 1 | 0 | 0402 | C17168
R5 | 1 | 10k | 0402 | C25744
D3 | 1 | Red LED | 0603 | C2286
C27 | 1 | 100n | 0402 | C1525 | 1867948
R11 | 1 | 512 | 0603 | C51224
U2 | 1 | STM32F746ZGT6 | Package_QFP:LQFP-144_20x20mm_P0.5mm | C90750
R15 | 1 | 10k | 0402 | C25744
R14 | 1 | 10k | 0402 | C25744
C41 | 1 | 100n | 0402 | C1525 | 1867948
C40 | 1 | 10u | 0603 | C19702 | 1867954
C38 | 1 | 10u | 0603 | C19702 | 1867954
C39 | 1 | 100n | 0603 | C14663
R16 | 1 | 4.99k | 0402 | C25903
J6 | 1 | 142-0701-851 | SamacSys_Parts:142-0701-851
R21 | 1 | 418 | 0402
R25 | 1 | 558 | 0402 | C67558
R17 | 1 | 4.52k | 0402
C46 | 1 | 1.3n | 0603
C42 | 1 | 1.3n | 0603
U3 | 1 | ADA4807-1 | SOT23-6
R22 | 1 | 406 | 0402
R26 | 1 | 541 | 0402
R18 | 1 | 4.39k | 0402
C47 | 1 | 1.1n | 0603
C43 | 1 | 1.1n | 0603
U4 | 1 | ADA4807-1 | SOT-23-6
R23 | 1 | 1.02k | 0402
R27 | 1 | 106 | 0402
R19 | 1 | 11k | 0402
C48 | 1 | 1.5n | 0603
C44 | 1 | 1.5n | 0603
U5 | 1 | ADA4807-1 | SOT-23-6
R24 | 1 | 966 | 0402
R28 | 1 | 100 | 0402
R20 | 1 | 10.4k | 0402
C49 | 1 | 1n | 0603 | C1588
C45 | 1 | 1n | 0603 | C1588
U6 | 1 | ADA4807-1 | SOT-23-6
J5 | 1 | PJS008-2003-1 | SamacSys_Parts:PJS00820031
R13 | 1 | 0 | 0402
R12 | 1 | NA | 0402
R6 | 1 | 47k | 0402 | C25792
R7 | 1 | 47k | 0402 | C25792
R8 | 1 | 47k | 0402 | C25792
R9 | 1 | 47k | 0402 | C25792
R10 | 1 | 47k | 0402 | C25792
IC1 | 1 | AD8031ARZ | SamacSys_Parts:SOIC127P600X175-8N
R1 | 1 | 2k2 | 0603 | C4190
D1 | 1 | Green LED | 0603 | C72043
S1 | 1 | TL1105CF160Q | SamacSys_Parts:TL1105CF160Q

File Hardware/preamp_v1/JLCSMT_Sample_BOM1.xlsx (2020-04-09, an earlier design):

Comment | Designator | Footprint | LCSC Part #（optional）
1uF | C2 | CAPC1608X95N
2.49kOhm | R9,R11 | RESC1608X63N
6.34kOhm | R15 | RESC1608X63N
10kOhm | R14 | RESC1608X63N
10pF | C9 | CAPC1608X95N
34.8kOhm | R1 | RESC1608X63N
35.7kOhm | R6 | RESC1608X63N
44.2kOhm | R12 | RESC1608X63N
47uF | C10,C11,C12,C13 | CAPAE660X790N
50kOhm | R2,R16 | RESC1608X63N
66.5kOhm | R13 | RESC1608X63N
100kOhm | R3,R4 | RESC1608X63N
100nF | C14 | CAPC1608X95N
100pF | C3,C4,C7,C8 | CAPC1608X95N
187Ohm | R8,R10 | RESC1608X63N
220uF | C1 | CAPAE660X540N
330Ohm | R17 | RESC1608X63N
282834-2 | BATTERY | TE_282834-2
HDR1X2 | BIASED SIGNAL,FILTER OUTPUT | HDR1X2
LMH6643MA | U5 | SOIC127P600X175-8N
LT1528CQ | U6 | TO170P1405X457-6N
OPA659IDBVR | U1,U2 | SOT95P280X145-5N
SMAh-edge | J1 | SMAh-edge
TLE2426CD | U3 | SOIC127P600X175-8N

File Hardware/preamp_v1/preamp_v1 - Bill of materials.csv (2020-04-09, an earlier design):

Ultiboard Information Export File
Design Name : OPA659_At1_6 - Bill of materials
Report Date : 14 November 2019
Report Time : 14:06
--------------------------------------------------------------------------------
VALUE | # | REFDES | FOOTPRINT | Package
1uF | 1 | C2 | CAPC1608X95N | IPC-7351\Chip-R0603
2.49kOhm | 2 | R9,R11 | RESC1608X63N | IPC-7351\Chip-R0603
6.34kOhm | 1 | R15 | RESC1608X63N | IPC-7351\Chip-R0603
10kOhm | 1 | R14 | RESC1608X63N | IPC-7351\Chip-R0603
10pF | 1 | C9 | CAPC1608X95N | IPC-7351\Chip-R0603
34.8kOhm | 1 | R1 | RESC1608X63N | IPC-7351\Chip-R0603
35.7kOhm | 1 | R6 | RESC1608X63N | IPC-7351\Chip-R0603
44.2kOhm | 1 | R12 | RESC1608X63N | IPC-7351\Chip-R0603
47uF | 4 | C10,C11,C12,C13 | CAPAE660X790N | IPC-7351\AlumElec-CaseD8
50kOhm | 2 | R2,R16 | RESC1608X63N | IPC-7351\Chip-R0603
66.5kOhm | 1 | R13 | RESC1608X63N | IPC-7351\Chip-R0603
100kOhm | 2 | R3,R4 | RESC1608X63N | IPC-7351\Chip-R0603
100nF | 1 | C14 | CAPC1608X95N | IPC-7351\Chip-C0603
100pF | 4 | C3,C4,C7,C8 | CAPC1608X95N | IPC-7351\Chip-R0603
187Ohm | 2 | R8,R10 | RESC1608X63N | IPC-7351\Chip-R0603
220uF | 1 | C1 | CAPAE660X540N | IPC-7351\AlumElec-CaseD
330Ohm | 1 | R17 | RESC1608X63N | IPC-7351\Chip-R0603
282834-2 | 1 | BATTERY | TE_282834-2 | TE Connectivity\282834-2
HDR1X2 | 2 | BIASED SIGNAL,FILTER OUTPUT | HDR1X2 | Generic\HDR1X2
LMH6643MA | 1 | U5 | SOIC127P600X175-8N | IPC-7351A\SOICNARROW-8(M08A)
LT1528CQ | 1 | U6 | TO170P1405X457-6N | IPC-7351\DD-5
OPA659IDBVR | 2 | U1,U2 | SOT95P280X145-5N | Texas Instruments\SOT-23-5(DBV)
SMAh-edge | 1 | J1 | SMAh-edge | generic\SMAh-edge
TLE2426CD | 1 | U3 | SOIC127P600X175-8N | IPC-7351\SOIC-D-8

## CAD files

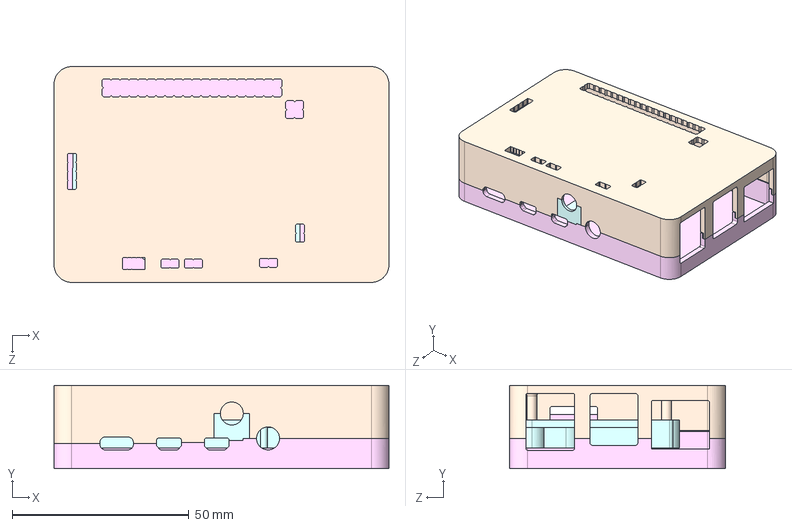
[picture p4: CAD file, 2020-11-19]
3D deisgns/Case.STEP
94.7 x 23.6 x 61.0 mm
Boss-Extrude6
case top
case bottom

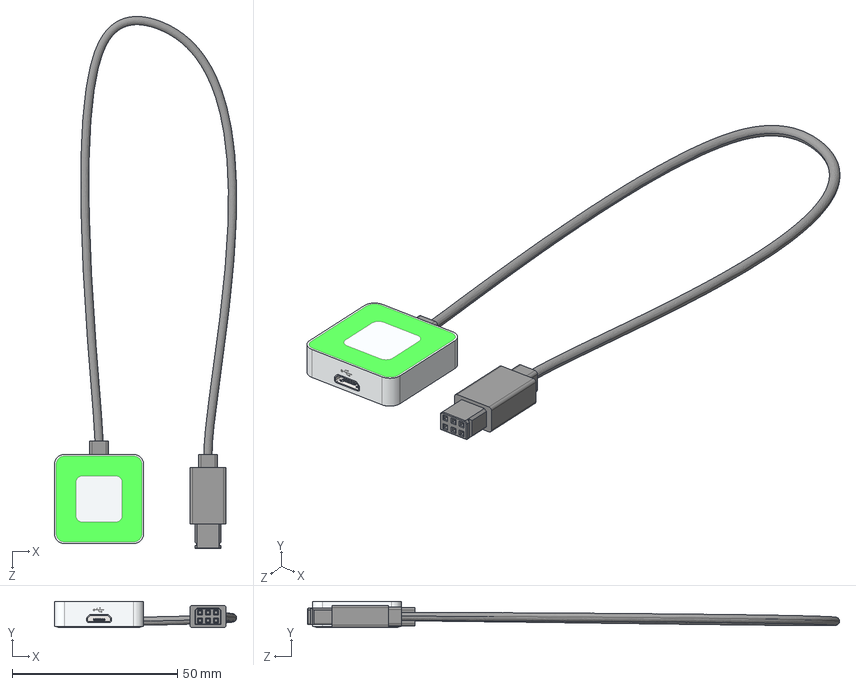
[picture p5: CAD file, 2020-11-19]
3D deisgns/Splashdrone Case/DJI - A3 - LED Module.STEP
55.1 x 8.00 x 161.2 mm
LED Pro^DJI - A3 - LED Module
CAN 6 Pin - Plug^DJI - A3 - LED Module
Cable#1^DJI - A3 - LED Module

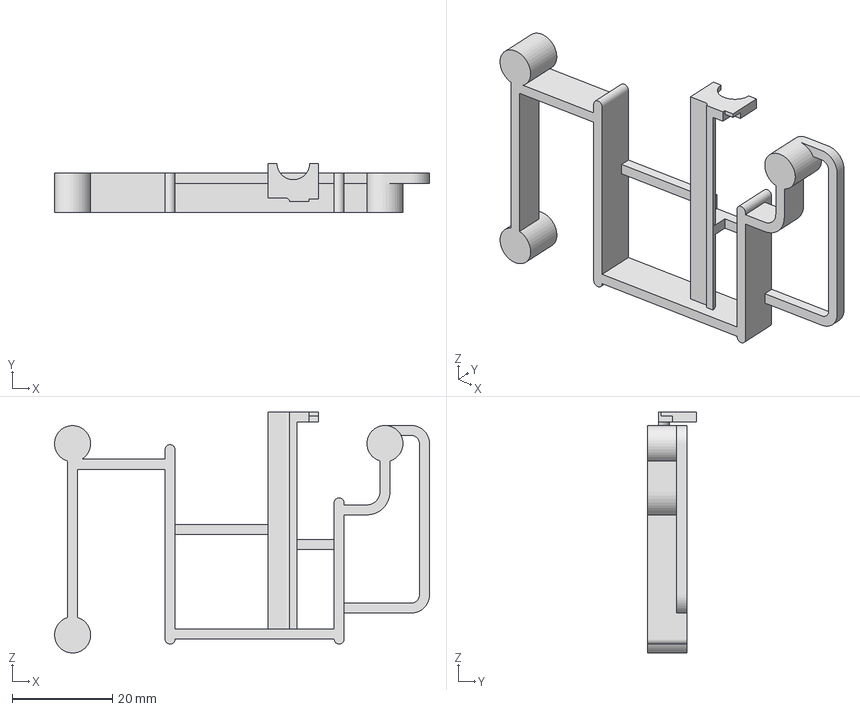
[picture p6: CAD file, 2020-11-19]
3D deisgns/midpart stl .3mf
74.7 x 9.80 x 48.0 mm

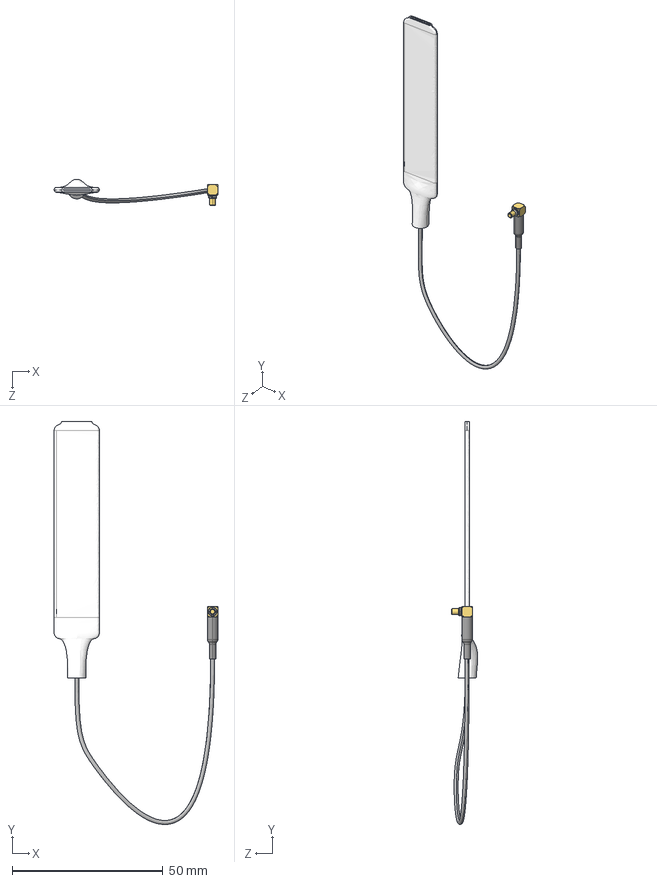
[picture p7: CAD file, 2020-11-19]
3D deisgns/Splashdrone Case/DJI - Lightbridge 2 - Antenna.STEP
54.2 x 133.5 x 8.75 mm
Antenna^DJI - Lightbridge 2 - Antenna
Ceble^DJI - Lightbridge 2 - Antenna
MMCX - Plug - 90deg Angle (Male)^DJI - Lightbridge 2 - Antenna

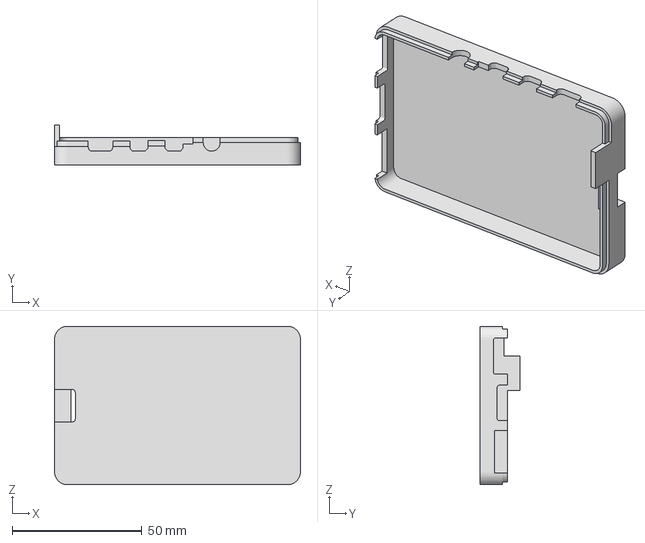
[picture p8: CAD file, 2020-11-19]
3D deisgns/lid stl.3mf
94.7 x 15.4 x 61.0 mm

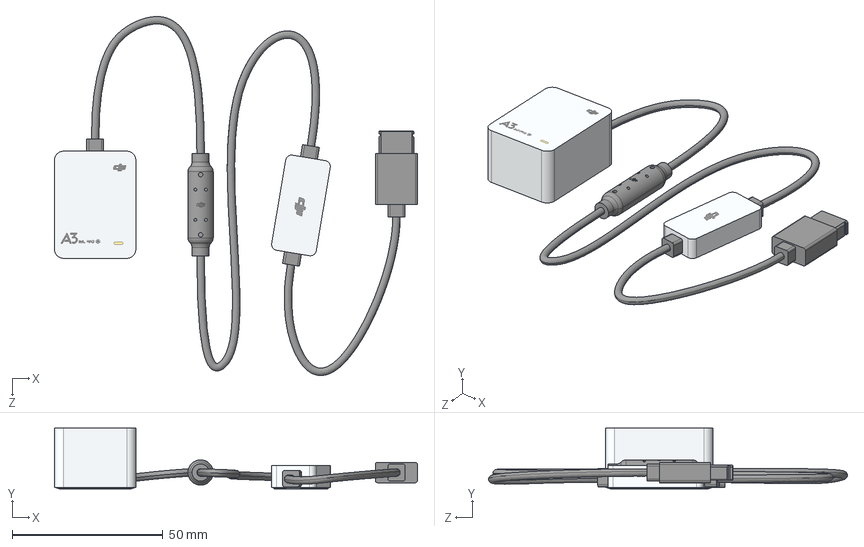
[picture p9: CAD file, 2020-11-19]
3D deisgns/Splashdrone Case/DJI - A3 - IMU PRO.STEP
120.5 x 20.1 x 119.2 mm
IMU Pro^DJI - A3 - IMU PRO
CAN Connector^DJI - A3 - IMU PRO
Noise Filter^DJI - A3 - IMU PRO
CAN 8 Pin - Plug^DJI - A3 - IMU PRO
Cable#1^DJI - A3 - IMU PRO
Cable#2^DJI - A3 - IMU PRO
Ceble#3^DJI - A3 - IMU PRO

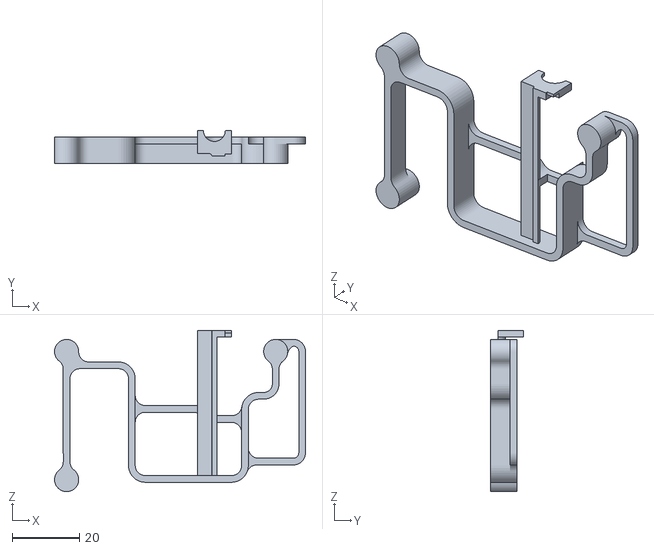
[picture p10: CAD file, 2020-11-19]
3D deisgns/midpart_2.STL
74.7 x 9.80 x 48.0

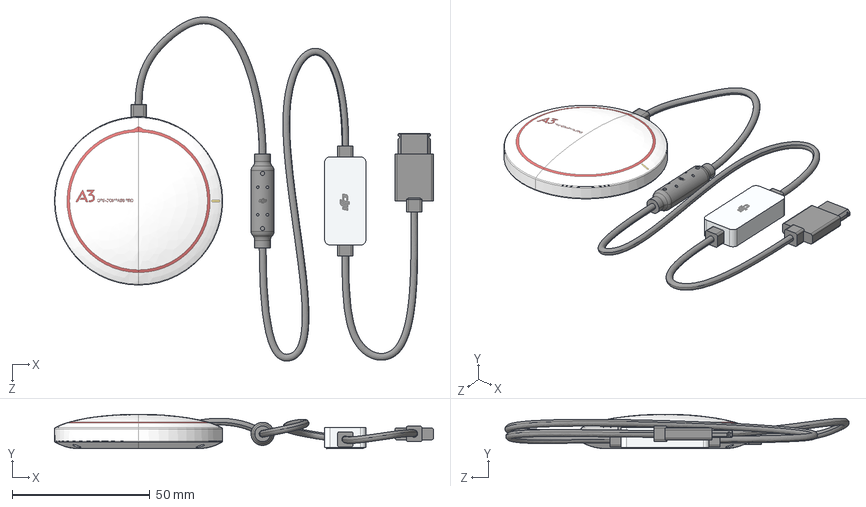
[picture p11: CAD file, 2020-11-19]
3D deisgns/Splashdrone Case/DJI - A3 - GPS-Compass PRO.STEP
137.5 x 12.5 x 124.9 mm
GPS-Compass PRO^DJI - A3 - GPS-Compass PRO
CAN Connector^DJI - A3 - GPS-Compass PRO
Noise Filter^DJI - A3 - GPS-Compass PRO
CAN 4 Pin - Plug^DJI - A3 - GPS-Compass PRO
Cable#1^DJI - A3 - GPS-Compass PRO
Cable#2^DJI - A3 - GPS-Compass PRO
Ceble#3^DJI - A3 - GPS-Compass PRO

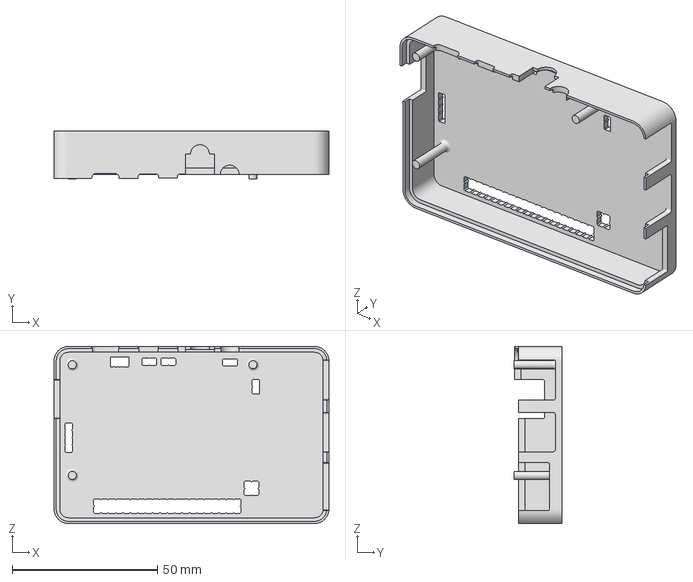
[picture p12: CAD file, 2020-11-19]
3D deisgns/base.3mf
94.7 x 16.5 x 61.0 mm

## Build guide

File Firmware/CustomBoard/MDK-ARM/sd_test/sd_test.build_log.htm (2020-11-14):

µVision Build Log

Tool Versions:

IDE-Version: µVision V5.28.0.0
Copyright (C) 2019 ARM Ltd and ARM Germany GmbH. All rights reserved.
License Information: dan babs, qwer, LIC=W96Y8-3NP3V-TJB6H-W1E0F-DTA56-693QP
 
Tool Versions:
Toolchain:       MDK-ARM Professional  Version: 5.28.0.0
Toolchain Path:  C:\Keil_v5\ARM\ARMCC\Bin
C Compiler:      Armcc.exe V5.06 update 6 (build 750)
Assembler:       Armasm.exe V5.06 update 6 (build 750)
Linker/Locator:  ArmLink.exe V5.06 update 6 (build 750)
Library Manager: ArmAr.exe V5.06 update 6 (build 750)
Hex Converter:   FromElf.exe V5.06 update 6 (build 750)
CPU DLL:         SARMCM3.DLL V5.28.0.0
Dialog DLL:      DCM.DLL V1.17.3.0
Target DLL:      STLink\ST-LINKIII-KEIL_SWO.dll V3.0.6.0
Dialog DLL:      TCM.DLL V1.36.2.0

Project:

C:\Users\Home\OneDrive\PhD\Phocoena-DAQ\Firmware\CustomBoard\MDK-ARM\sd_test.uvprojx
Project File Date:  09/14/2020

Output:

*** Using Compiler 'V5.06 update 6 (build 750)', folder: 'C:\Keil_v5\ARM\ARMCC\Bin'
Build target 'sd_test'
compiling freertos.c...
linking...
Program Size: Code=38176 RO-data=78604 RW-data=200 ZI-data=293472  
FromELF: creating hex file...
"sd_test\sd_test.axf" - 0 Error(s), 0 Warning(s).

Software Packages used:

Package Vendor: ARM
                http://www.keil.com/pack/ARM.CMSIS.5.6.0.pack
                ARM.CMSIS.5.6.0
                CMSIS (Cortex Microcontroller Software Interface Standard)
   * Component: CORE Version: 5.3.0
   * Component: DSP Variant: Library Version: 1.7.0

Package Vendor: Keil
                https://www.keil.com/pack/Keil.STM32F7xx_DFP.2.12.0.pack
                Keil.STM32F7xx_DFP.2.12.0
                STMicroelectronics STM32F7 Series Device Support, Drivers and Examples

Collection of Component include folders:

  .\RTE\_sd_test
  C:\Users\Home\AppData\Local\Arm\Packs\ARM\CMSIS\5.6.0\CMSIS\Core\Include
  C:\Users\Home\AppData\Local\Arm\Packs\ARM\CMSIS\5.6.0\CMSIS\DSP\Include
  C:\Users\Home\AppData\Local\Arm\Packs\Keil\STM32F7xx_DFP\2.12.0\Drivers\CMSIS\Device\ST\STM32F7xx\Include

Collection of Component Files used:

   * Component: ARM::CMSIS:CORE:5.3.0

   * Component: ARM::CMSIS:DSP:Library:1.7.0
      Include file:  CMSIS\DSP\Include\arm_math.h
      Library file:  CMSIS\DSP\Lib\ARM\arm_cortexM7lfsp_math.lib
Build Time Elapsed:  00:00:03

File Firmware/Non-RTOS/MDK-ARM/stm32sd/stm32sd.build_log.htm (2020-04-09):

µVision Build Log

Tool Versions:

IDE-Version: µVision V5.24.2.0
Copyright (C) 2017 ARM Ltd and ARM Germany GmbH. All rights reserved.
License Information: Man aak, kdjk, LIC=HF8TG-V2SB0-GNHA5-G7R85-LU2X9-Q24GB
 
Tool Versions:
Toolchain:       MDK-ARM Professional  Version: 5.24.1
Toolchain Path:  C:\Keil_v5\ARM\ARMCC\Bin
C Compiler:      Armcc.exe V5.06 update 5 (build 528)
Assembler:       Armasm.exe V5.06 update 5 (build 528)
Linker/Locator:  ArmLink.exe V5.06 update 5 (build 528)
Library Manager: ArmAr.exe V5.06 update 5 (build 528)
Hex Converter:   FromElf.exe V5.06 update 5 (build 528)
CPU DLL:         SARMCM3.DLL V5.24.1
Dialog DLL:      DCM.DLL V1.16.0.0
Target DLL:      STLink\ST-LINKIII-KEIL_SWO.dll V3.0.1.0
Dialog DLL:      TCM.DLL V1.32.0.0

Project:

C:\Users\mogun\Desktop\stm32sd\stm32sd\MDK-ARM\stm32sd.uvprojx
Project File Date:  11/05/2019

Output:

*** Using Compiler 'V5.06 update 5 (build 528)', folder: 'C:\Keil_v5\ARM\ARMCC\Bin'
Build target 'stm32sd'
compiling main.c...
linking...
Program Size: Code=26840 RO-data=12504 RW-data=112 ZI-data=36952  
FromELF: creating hex file...
"stm32sd\stm32sd.axf" - 0 Error(s), 0 Warning(s).

Software Packages used:

Package Vendor: ARM
                http://www.keil.com/pack/ARM.CMSIS.5.6.0.pack
                ARM.CMSIS.5.6.0
                CMSIS (Cortex Microcontroller Software Interface Standard)
   * Component: DSP Variant: Library Version: 1.7.0
   * Component: CORE Version: 5.3.0

Package Vendor: Keil
                https://www.keil.com/pack/Keil.STM32F7xx_DFP.2.12.0.pack
                Keil.STM32F7xx_DFP.2.12.0
                STMicroelectronics STM32F7 Series Device Support, Drivers and Examples

Collection of Component include folders:

  .\RTE\_stm32sd
  C:\Keil_v5\ARM\PACK\ARM\CMSIS\5.6.0\CMSIS\Core\Include
  C:\Keil_v5\ARM\PACK\ARM\CMSIS\5.6.0\CMSIS\DSP\Include
  C:\Keil_v5\ARM\PACK\Keil\STM32F7xx_DFP\2.12.0\Drivers\CMSIS\Device\ST\STM32F7xx\Include

Collection of Component Files used:

   * Component: ARM::CMSIS:DSP:Library:1.7.0
      Include file:  CMSIS\DSP\Include\arm_math.h
      Library file:  CMSIS\DSP\Lib\ARM\arm_cortexM7lfsp_math.lib

   * Component: ARM::CMSIS:CORE:5.3.0
Build Time Elapsed:  00:00:06

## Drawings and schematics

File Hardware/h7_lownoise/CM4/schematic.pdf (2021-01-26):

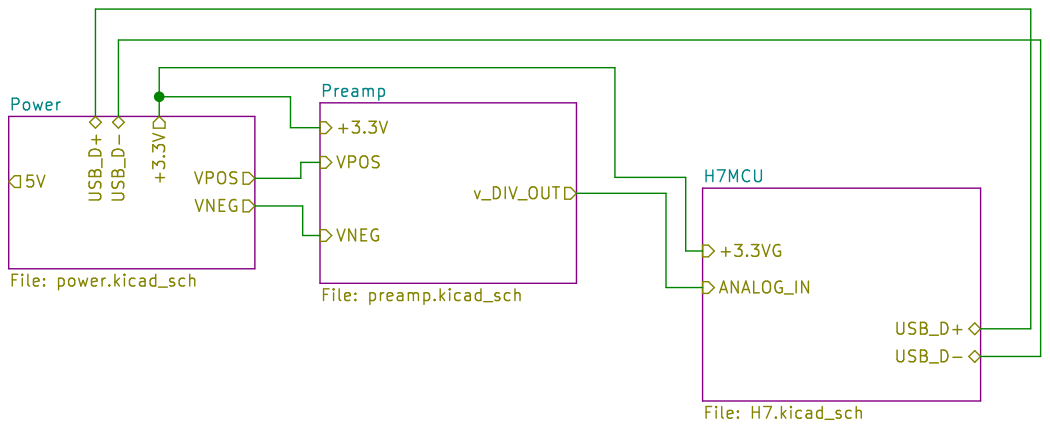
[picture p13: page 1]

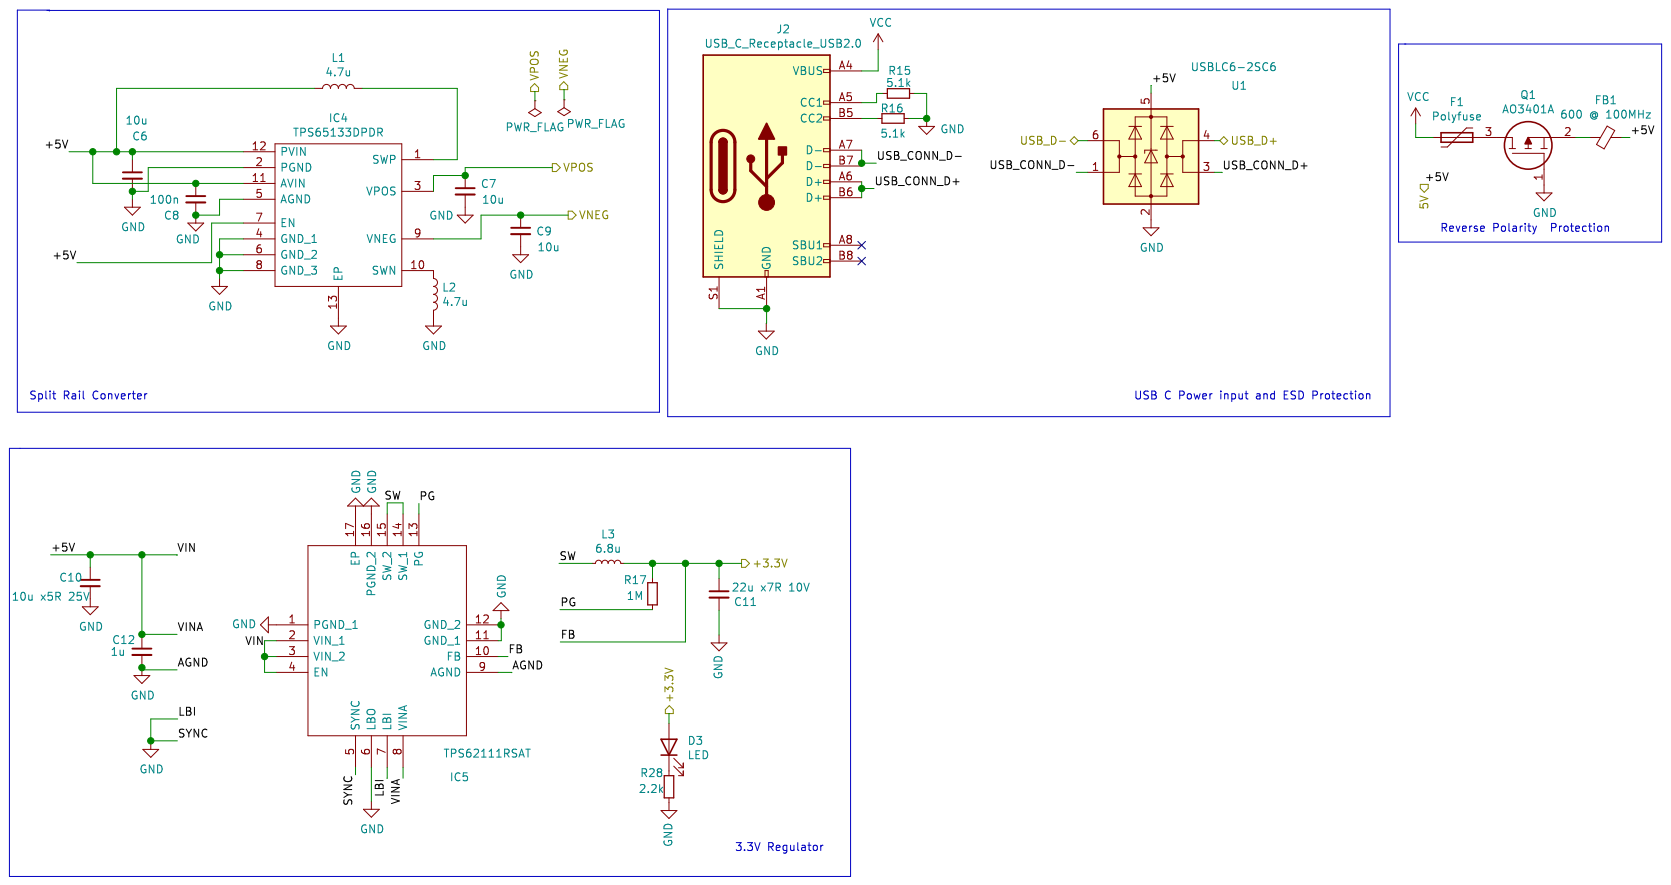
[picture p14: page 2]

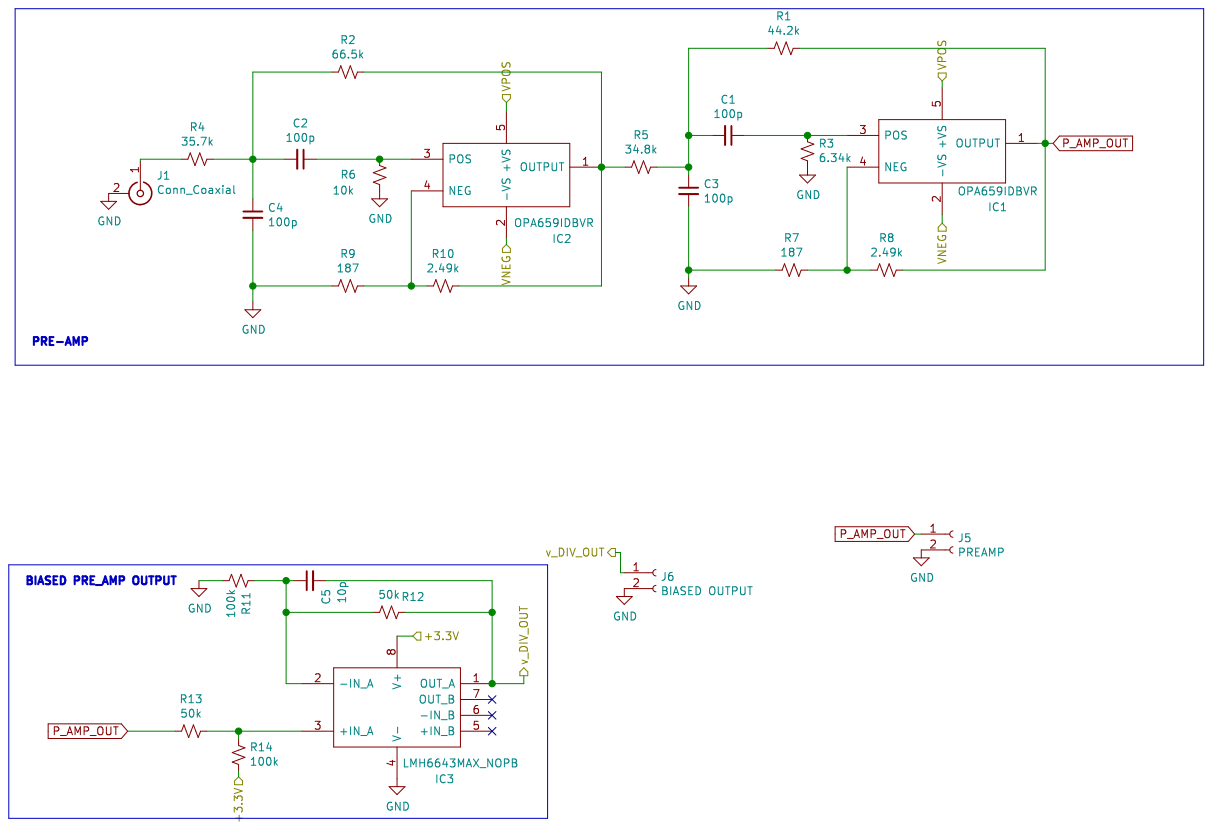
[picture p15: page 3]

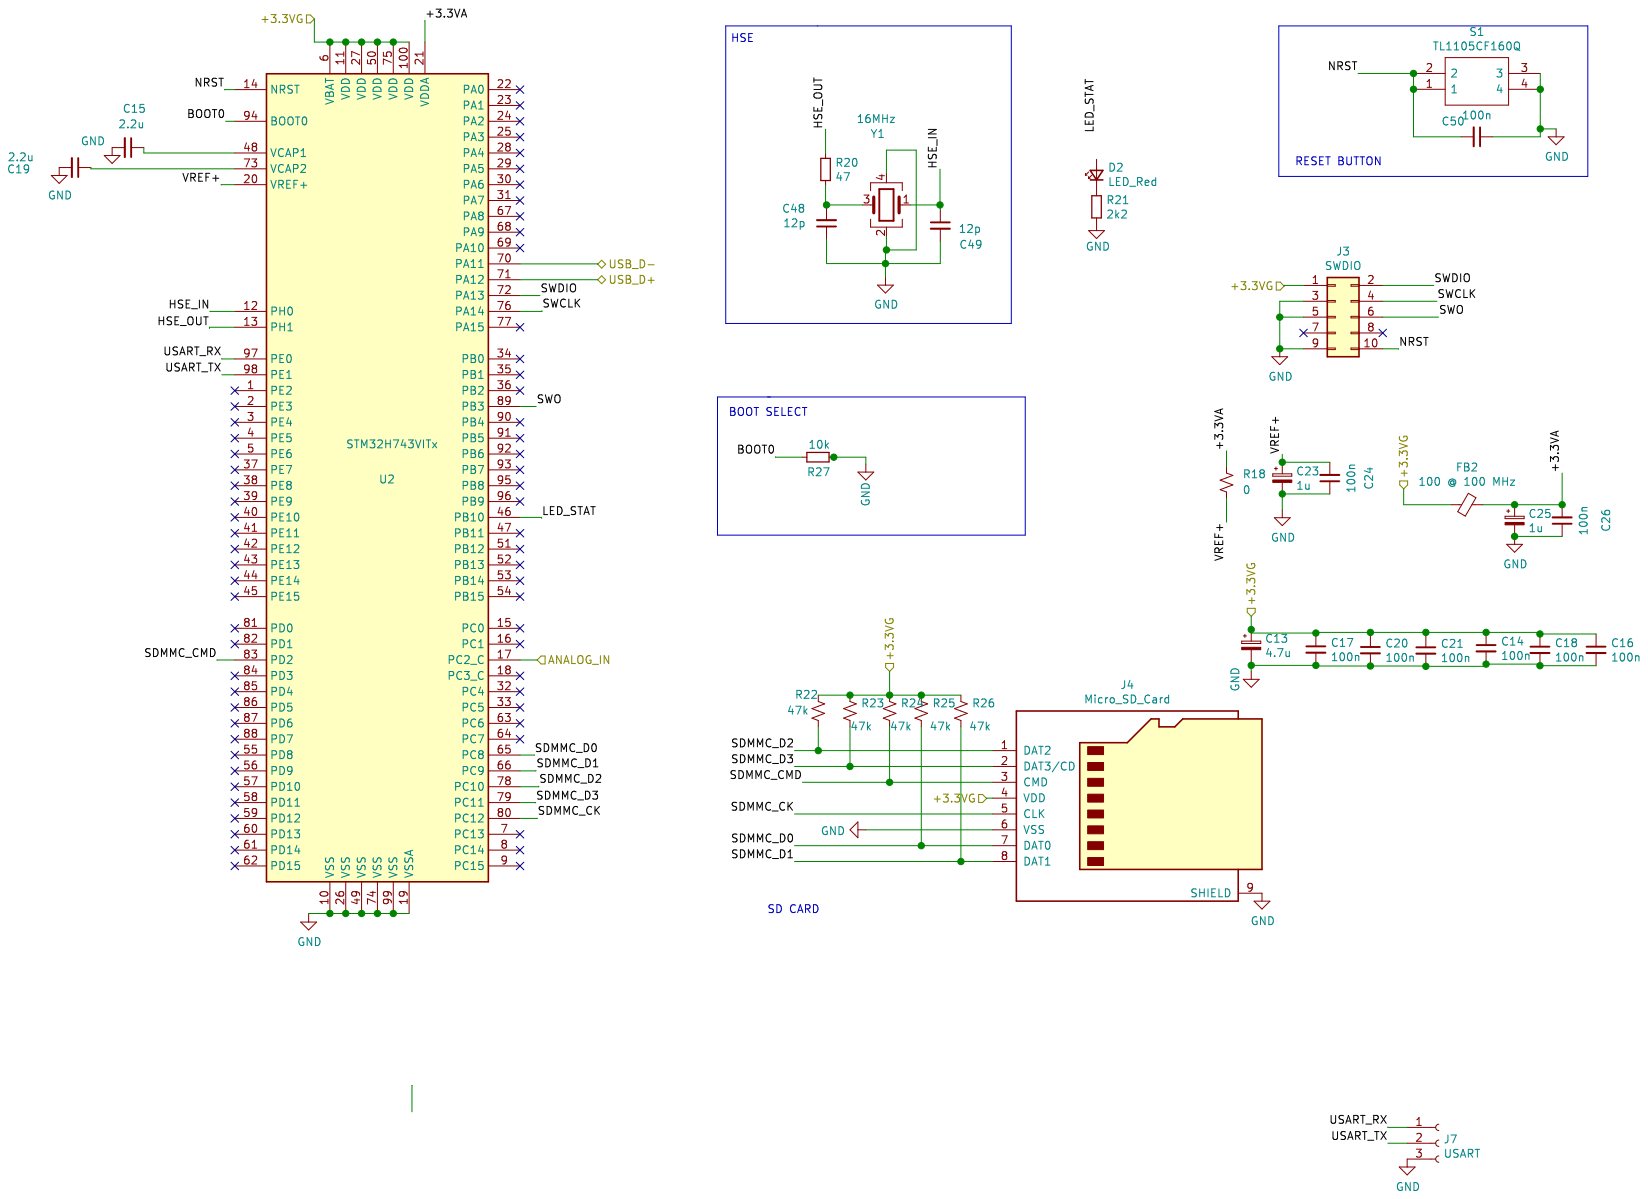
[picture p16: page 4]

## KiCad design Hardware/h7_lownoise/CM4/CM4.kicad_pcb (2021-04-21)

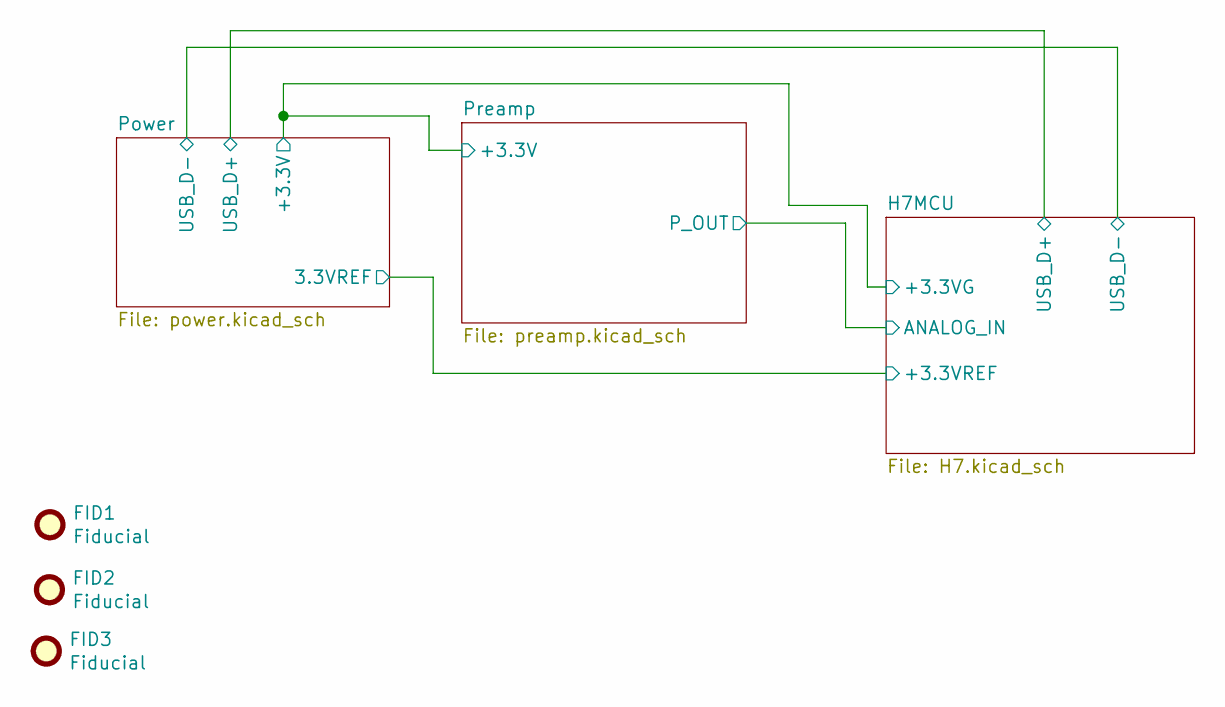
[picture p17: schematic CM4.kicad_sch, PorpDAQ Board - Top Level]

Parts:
FID1, FID2, FID3: Fiducial; Fiducial_0.5mm_Mask1.5mm

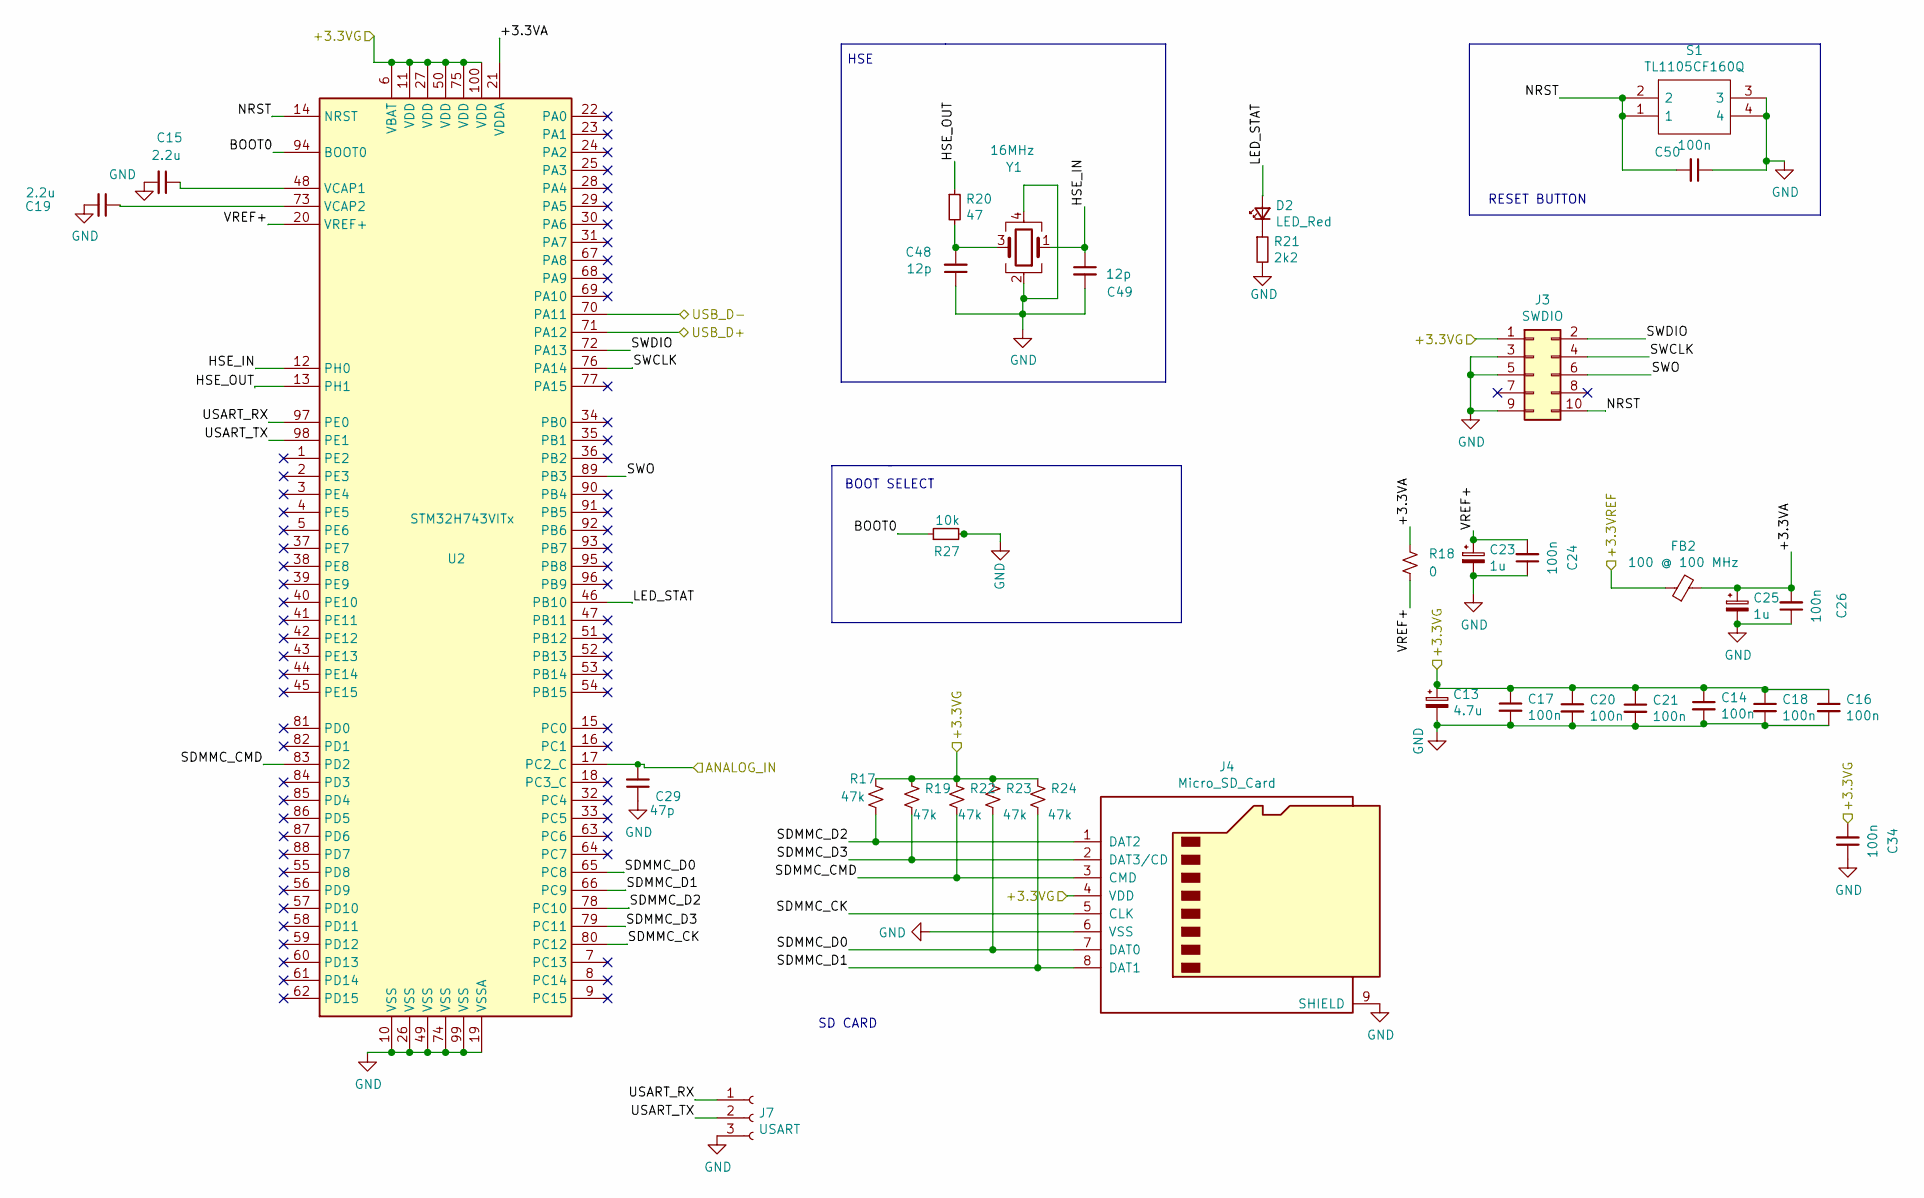
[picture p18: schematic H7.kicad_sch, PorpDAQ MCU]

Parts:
C13: 4.7u; CP_EIA-3216-18_Kemet-A; LCSC Part # C7187
C14, C16, C17, C18, C20, C21, C24, C26, C34, C50: 100n; C_0402_1005Metric; LCSC Part # C1525
C15, C19: 2.2u; C_1206_3216Metric; LCSC Part # C50254
C23, C25: 1u; CP_EIA-3216-18_Kemet-A; LCSC Part # C7176
C29: 47p; C_0402_1005Metric; LCSC Part # C1567
C48, C49: 12p; C_0402_1005Metric; LCSC Part # C1547
D2: LED_Red; LED_0603_1608Metric; LCSC Part # C2286
FB2: 100 @ 100 MHz; L_0603_1608Metric; LCSC Part # C74325
J3: SWDIO; PinHeader_2x05_P1.27mm_Vertical
J4: Micro_SD_Card; microSD_HC_Hirose_DM3AT-SF-PEJM5
J7: USART; PinHeader_1x03_P2.54mm_Vertical
R17, R19, R22, R23, R24: 47k; R_0402_1005Metric; LCSC Part # C25792
R18: 0; R_0402_1005Metric; LCSC Part # C17168
R20: 47; R_0402_1005Metric; LCSC Part # C25118
R21: 2k2; R_0603_1608Metric; LCSC Part # C4190
R27: 10k; R_0402_1005Metric; LCSC Part # C25744
S1: TL1105CF160Q; Manufacturer_Part_Number TL1105CF160Q; Mouser Part Number 612-TL1105C
U2: STM32H743VITx; LQFP-100_14x14mm_P0.5mm
Y1: 16MHz; Crystal_SMD_3225-4Pin_3.2x2.5mm; LCSC Part # C13738

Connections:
/3.3VREF: FB2.1; also elsewhere on the board
/+3.3V: C13.1, C14.1, C16.1, C17.1, C18.1, C20.1, C21.1, C34.2, J3.1, J4.4 (VDD), R17.2, R19.2, R22.2, R23.2, R24.2, U2.6 (VBAT), U2.11 (VDD), U2.27 (VDD), U2.50 (VDD), U2.75 (VDD), U2.100 (VDD); also elsewhere on the board
/H7MCU/+3.3VA: C25.1, C26.2, FB2.2, R18.2, U2.21 (VDDA)
/H7MCU/BOOT0: R27.1, U2.94 (BOOT0)
/H7MCU/HSE_IN: C49.1, U2.12 (PH0), Y1.1
/H7MCU/HSE_OUT: R20.1, U2.13 (PH1)
/H7MCU/LED_STAT: D2.2 (A), U2.46 (PB10)
/H7MCU/NRST: C50.2, J3.10, S1.1, S1.2, U2.14 (NRST)
/H7MCU/SDMMC_CK: J4.5 (CLK), U2.80 (PC12)
/H7MCU/SDMMC_CMD: J4.3 (CMD), R22.1, U2.83 (PD2)
/H7MCU/SDMMC_D0: J4.7 (DAT0), R23.1, U2.65 (PC8)
/H7MCU/SDMMC_D1: J4.8 (DAT1), R24.1, U2.66 (PC9)
/H7MCU/SDMMC_D2: J4.1 (DAT2), R17.1, U2.78 (PC10)
/H7MCU/SDMMC_D3: J4.2 (DAT3/CD), R19.1, U2.79 (PC11)
/H7MCU/SWCLK: J3.4, U2.76 (PA14)
/H7MCU/SWDIO: J3.2, U2.72 (PA13)
/H7MCU/SWO: J3.6, U2.89 (PB3)
/H7MCU/USART_RX: J7.1, U2.97 (PE0)
/H7MCU/USART_TX: J7.2, U2.98 (PE1)
/H7MCU/VREF+: C23.1, C24.2, R18.1, U2.20 (VREF+)
/P_OUT: C29.2, U2.17 (PC2_C); also elsewhere on the board
/USB_D+: U2.71 (PA12); also elsewhere on the board
/USB_D-: U2.70 (PA11); also elsewhere on the board
GND: C13.2, C14.2, C15.2, C16.2, C17.2, C18.2, C19.2, C20.2, C21.2, C23.2, C24.1, C25.2, C26.1, C29.1, C34.1, C48.1, C49.2, C50.1, J3.3, J3.5, J3.9, J4.6 (VSS), J4.9 (SHIELD), J7.3, R21.2, R27.2, S1.3, S1.4, U2.10 (VSS), U2.19 (VSSA), U2.26 (VSS), U2.49 (VSS), U2.74 (VSS), U2.99 (VSS), Y1.2, Y1.4; also elsewhere on the board
unnamed: C15.1, U2.48 (VCAP1)
unnamed: C19.1, U2.73 (VCAP2)
unnamed: C48.2, R20.2, Y1.3
unnamed: D2.1 (K), R21.1
no_connect_58: J3.7
no_connect_59: J3.8
no_connect_60: U2.1 (PE2)
no_connect_61: U2.15 (PC0)
no_connect_62: U2.16 (PC1)
no_connect_63: U2.18 (PC3_C)
no_connect_64: U2.2 (PE3)
no_connect_65: U2.22 (PA0)
no_connect_66: U2.23 (PA1)
no_connect_67: U2.24 (PA2)
no_connect_68: U2.25 (PA3)
no_connect_69: U2.28 (PA4)
no_connect_70: U2.29 (PA5)
no_connect_71: U2.3 (PE4)
no_connect_72: U2.30 (PA6)
no_connect_73: U2.31 (PA7)
no_connect_74: U2.32 (PC4)
no_connect_75: U2.33 (PC5)
no_connect_76: U2.34 (PB0)
no_connect_77: U2.35 (PB1)
no_connect_78: U2.36 (PB2)
no_connect_79: U2.37 (PE7)
no_connect_80: U2.38 (PE8)
no_connect_81: U2.39 (PE9)
no_connect_82: U2.4 (PE5)
no_connect_83: U2.40 (PE10)
no_connect_84: U2.41 (PE11)
no_connect_85: U2.42 (PE12)
no_connect_86: U2.43 (PE13)
no_connect_87: U2.44 (PE14)
no_connect_88: U2.45 (PE15)
no_connect_89: U2.47 (PB11)
no_connect_90: U2.5 (PE6)
no_connect_91: U2.51 (PB12)
no_connect_92: U2.52 (PB13)
no_connect_93: U2.53 (PB14)
no_connect_94: U2.54 (PB15)
no_connect_95: U2.55 (PD8)
no_connect_96: U2.56 (PD9)
no_connect_97: U2.57 (PD10)
no_connect_98: U2.58 (PD11)
no_connect_99: U2.59 (PD12)
no_connect_100: U2.60 (PD13)
no_connect_101: U2.61 (PD14)
no_connect_102: U2.62 (PD15)
no_connect_103: U2.63 (PC6)
no_connect_104: U2.64 (PC7)
no_connect_105: U2.67 (PA8)
no_connect_106: U2.68 (PA9)
no_connect_107: U2.69 (PA10)
no_connect_108: U2.7 (PC13)
no_connect_109: U2.77 (PA15)
no_connect_110: U2.8 (PC14)
no_connect_111: U2.81 (PD0)
no_connect_112: U2.82 (PD1)
no_connect_113: U2.84 (PD3)
no_connect_114: U2.85 (PD4)
no_connect_115: U2.86 (PD5)
no_connect_116: U2.87 (PD6)
no_connect_117: U2.88 (PD7)
no_connect_118: U2.9 (PC15)
no_connect_119: U2.90 (PB4)
no_connect_120: U2.91 (PB5)
no_connect_121: U2.92 (PB6)
no_connect_122: U2.93 (PB7)
no_connect_123: U2.95 (PB8)
no_connect_124: U2.96 (PB9)

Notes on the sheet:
SD CARD
BOOT SELECT
HSE
RESET BUTTON

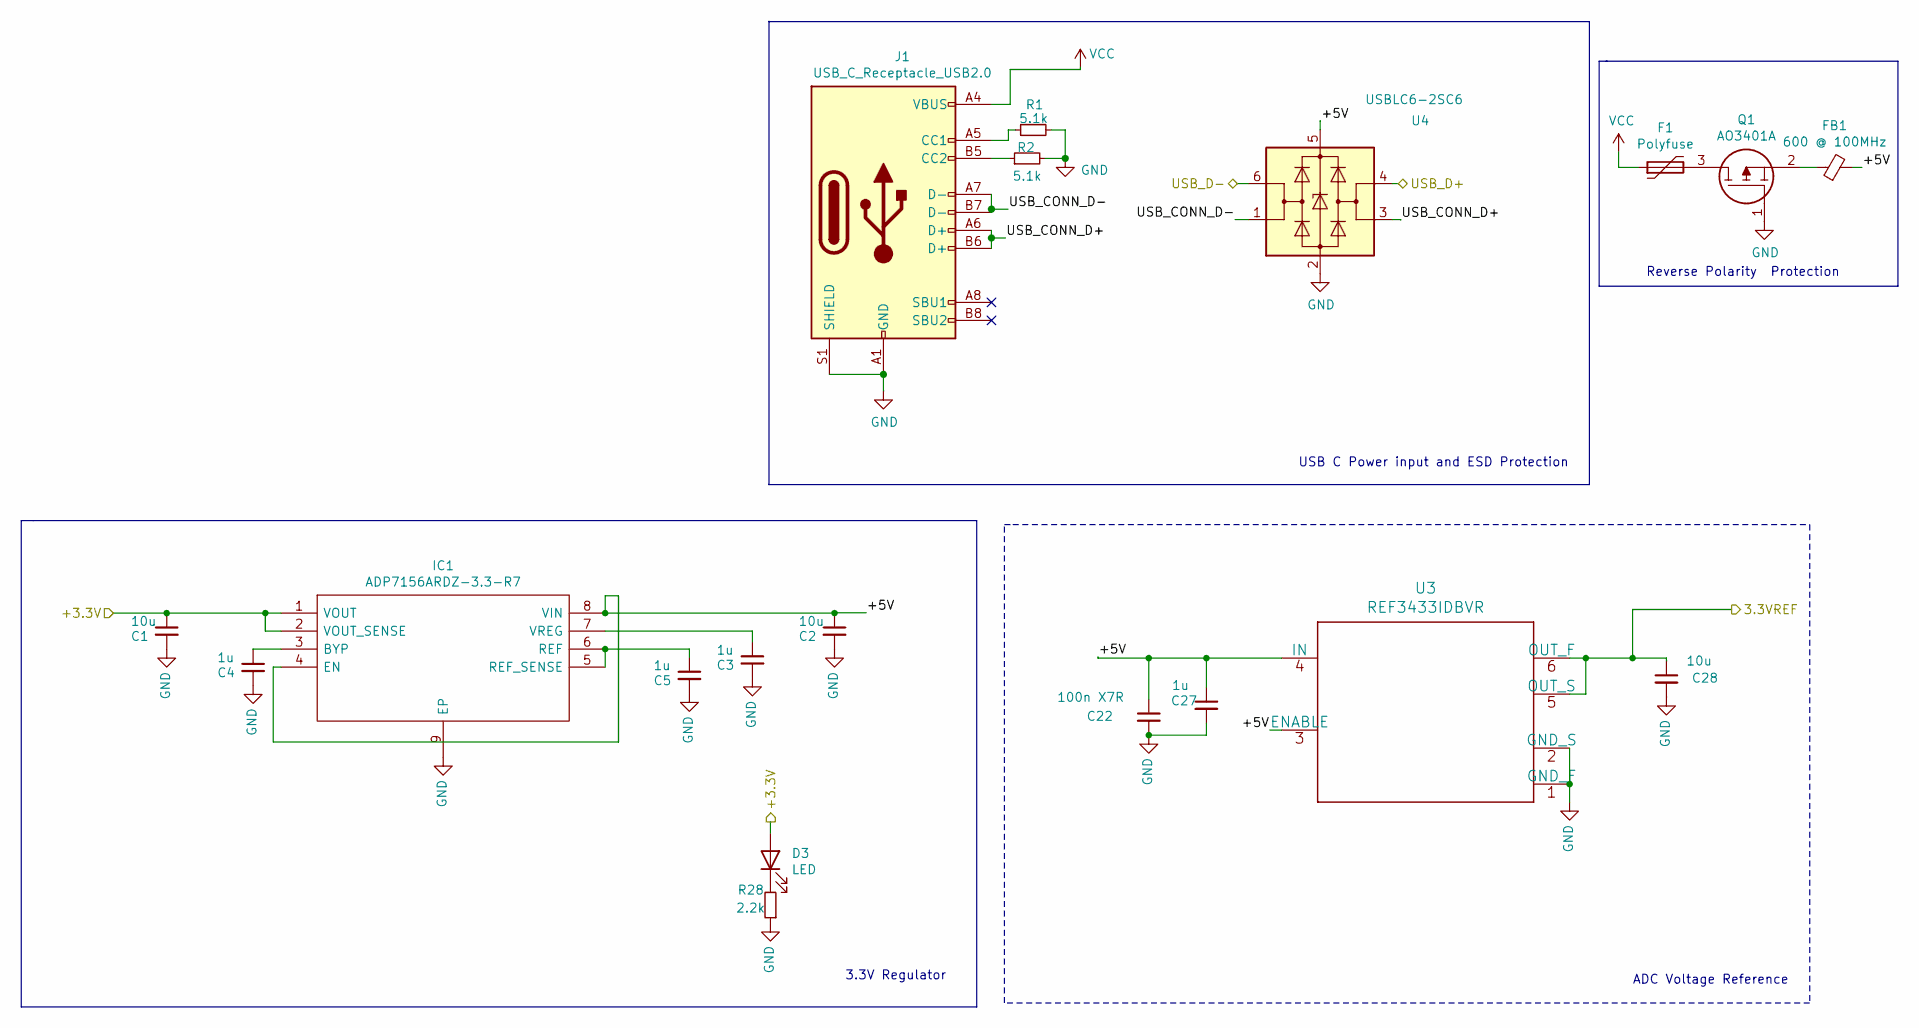
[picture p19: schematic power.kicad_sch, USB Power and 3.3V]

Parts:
C1, C2, C28: 10u; C_0603_1608Metric; LCSC Part # C19702
C3, C4, C5, C27: 1u; C_0603_1608Metric; LCSC Part # C15849
C22: 100n X7R; C_0603_1608Metric; LCSC Part # C14663
D3: LED; LED_0603_1608Metric; LCSC Part # C72043
F1: Polyfuse; Fuse_1206_3216Metric; LCSC Part # C369159
FB1: 600 @ 100MHz; L_0805_2012Metric; LCSC Part # C1017
IC1: ADP7156ARDZ-3.3-R7; SOIC127P600X175-9N; Manufacturer_Part_Number ADP7156ARDZ-3.3-R7; Mouser Part Number 584-ADP7156ARDZ3.3R7
J1: USB_C_Receptacle_USB2.0; TYPE-C-31-M-12; LCSC Part # C165948
Q1: AO3401A; SOT95P280X125-3N; Manufacturer_Part_Number AO3401A; LCSC Part # C15127
R1, R2: 5.1k; R_1206_3216Metric; LCSC Part # C26033
R28: 2.2k; R_0603_1608Metric; LCSC Part # C4190
U3: REF3433IDBVR
U4: USBLC6-2SC6; SOT-23-6; LCSC Part # C7519

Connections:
/3.3VREF: C28.1, U3.5 (OUT_S), U3.6 (OUT_F); also elsewhere on the board
/+3.3V: C1.1, D3.2 (A), IC1.1 (VOUT), IC1.2 (VOUT_SENSE); also elsewhere on the board
/Power/+5V: C2.1, C22.1, C27.1, FB1.2, IC1.4 (EN), IC1.8 (VIN), U3.3 (ENABLE), U3.4 (IN), U4.5 (VBUS)
/Power/USB_CONN_D+: J1.A6 (D+), J1.B6 (D+), U4.3 (I/O2)
/Power/USB_CONN_D-: J1.A7 (D-), J1.B7 (D-), U4.1 (I/O1)
/USB_D+: U4.4 (I/O2); also elsewhere on the board
/USB_D-: U4.6 (I/O1); also elsewhere on the board
GND: C1.2, C2.2, C3.2, C4.2, C5.2, C22.2, C27.2, C28.2, IC1.9 (EP), J1.A1 (GND), J1.A12 (GND), J1.B1 (GND), J1.B12 (GND), J1.S1 (SHIELD), Q1.1, R1.2, R2.2, R28.1, U3.1 (GND_F), U3.2 (GND_S), U4.2 (GND); also elsewhere on the board
unnamed: C3.1, IC1.7 (VREG)
unnamed: C4.1, IC1.3 (BYP)
unnamed: C5.1, IC1.5 (REF_SENSE), IC1.6 (REF)
unnamed: D3.1 (K), R28.2
unnamed: F1.2, Q1.3
unnamed: FB1.1, Q1.2
unnamed: J1.A5 (CC1), R1.1
unnamed: J1.B5 (CC2), R2.1
VCC: F1.1, J1.A4 (VBUS), J1.A9 (VBUS), J1.B4 (VBUS), J1.B9 (VBUS)
no_connect_56: J1.A8 (SBU1)
no_connect_57: J1.B8 (SBU2)

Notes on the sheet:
3.3V Regulator
USB C Power input and ESD Protection
ADC Voltage Reference
Reverse Polarity Protection

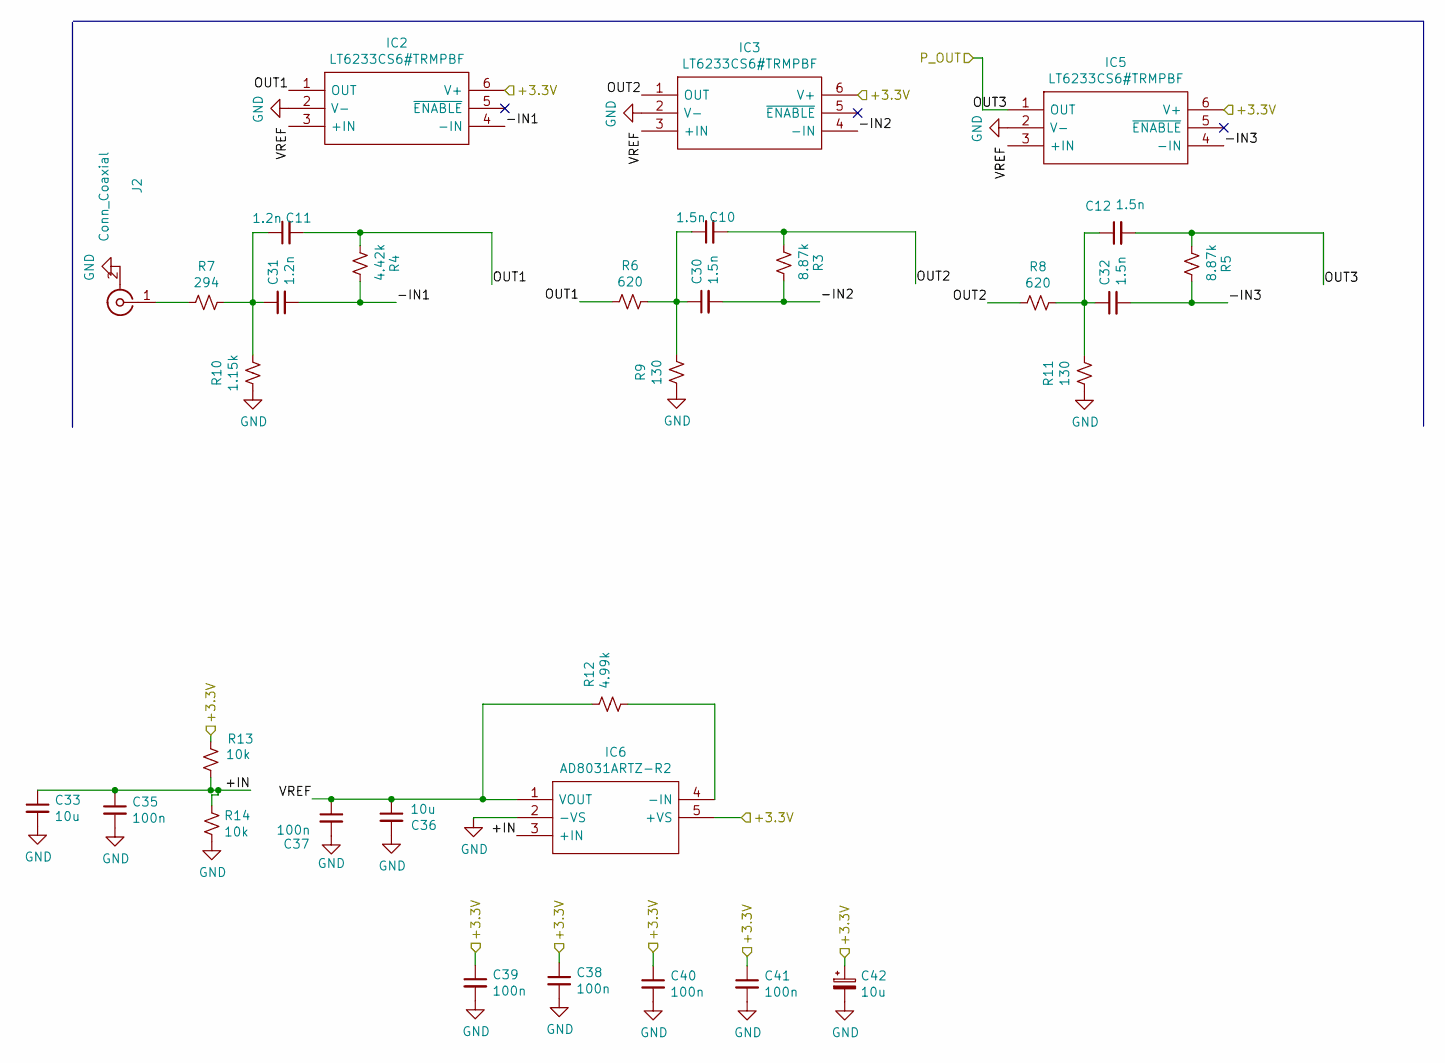
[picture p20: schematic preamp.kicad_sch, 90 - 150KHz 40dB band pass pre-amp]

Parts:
C10, C12, C30, C32: 1.5n; C_0402_1005Metric; LCSC Part # C23967
C11, C31: 1.2n; C_0402_1005Metric; LCSC Part # C16529
C33, C36: 10u; C_0603_1608Metric; LCSC Part # C19702
C35, C37, C38, C39, C40, C41: 100n; C_0603_1608Metric; LCSC Part # C14663
C42: 10u; CP_EIA-3216-18_Kemet-A; LCSC Part # c7171
IC2, IC3, IC5: LT6233CS6#TRMPBF; SOT95P280X100-6N; Manufacturer_Part_Number LT6233CS6#TRMPBF; Mouser Part Number 584-LT6233CS6#TRMPBF
IC6: AD8031ARTZ-R2; SOT95P280X145-5N; Manufacturer_Part_Number AD8031ARTZ-R2; Mouser Part Number 584-AD8031ARTZ-R2
J2: Conn_Coaxial; SMA_Wurth_60312002114503_Vertical
R3, R5: 8.87k; R_0402_1005Metric; LCSC Part # C36953
R4: 4.42k; R_0402_1005Metric; LCSC Part # C52269
R6, R8: 620; R_0402_1005Metric; LCSC Part # C4961
R7: 294; R_0402_1005Metric; LCSC Part # C270618
R9, R11: 130; R_0402_1005Metric; LCSC Part # C270649
R10: 1.15k; R_0402_1005Metric; LCSC Part # C29401
R12: 4.99k; R_0603_1608Metric; LCSC Part # C23046
R13, R14: 10k; R_0603_1608Metric; LCSC Part # C25804

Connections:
/+3.3V: C38.1, C39.1, C40.1, C41.1, C42.1, IC2.6 (V+), IC3.6 (V+), IC5.6 (V+), IC6.5 (+VS), R13.1; also elsewhere on the board
/P_OUT: C12.2, IC5.1 (OUT), R5.2; also elsewhere on the board
/Preamp/+IN: C33.1, C35.1, IC6.3 (+IN), R13.2, R14.1
/Preamp/-IN1: C31.2, IC2.4 (-IN), R4.1
/Preamp/-IN2: C30.2, IC3.4 (-IN), R3.1
/Preamp/-IN3: C32.2, IC5.4 (-IN), R5.1
/Preamp/OUT1: C11.2, IC2.1 (OUT), R4.2, R6.1
/Preamp/OUT2: C10.2, IC3.1 (OUT), R3.2, R8.1
/Preamp/VREF: C36.1, C37.1, IC2.3 (+IN), IC3.3 (+IN), IC5.3 (+IN), IC6.1 (VOUT), R12.1
GND: C33.2, C35.2, C36.2, C37.2, C38.2, C39.2, C40.2, C41.2, C42.2, IC2.2 (V-), IC3.2 (V-), IC5.2 (V-), IC6.2 (-VS), J2.2 (Ext), R9.1, R10.1, R11.1, R14.2; also elsewhere on the board
unnamed: C10.1, C30.1, R6.2, R9.2
unnamed: C11.1, C31.1, R7.2, R10.2
unnamed: C12.1, C32.1, R8.2, R11.2
unnamed: IC6.4 (-IN), R12.2
unnamed: J2.1 (In), R7.1
no_connect_53: IC2.5 (~ENABLE)
no_connect_54: IC3.5 (~ENABLE)
no_connect_55: IC5.5 (~ENABLE)

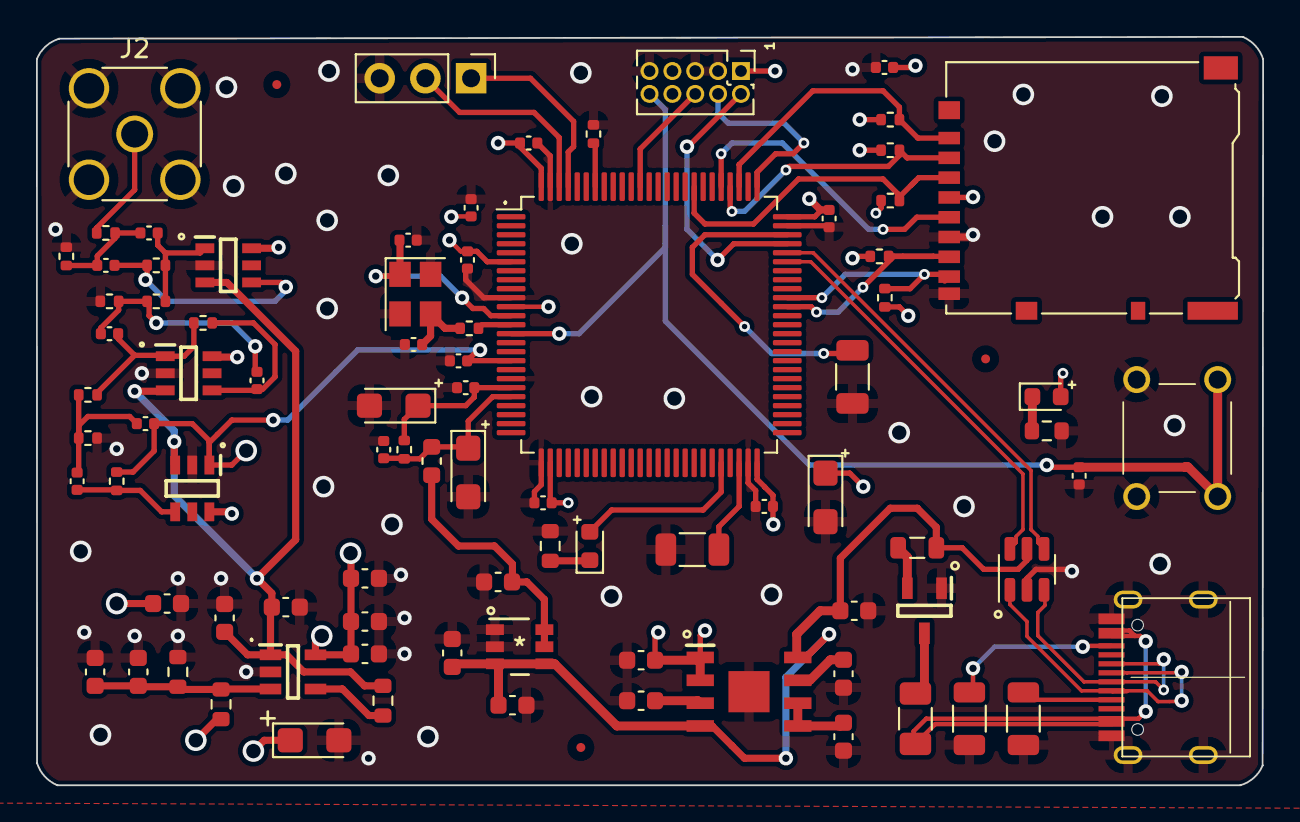
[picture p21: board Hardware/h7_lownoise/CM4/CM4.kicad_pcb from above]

Board: 4 copper layers, 68.2 x 41.6 mm, 89 parts (0 on the bottom side), 52 nets.

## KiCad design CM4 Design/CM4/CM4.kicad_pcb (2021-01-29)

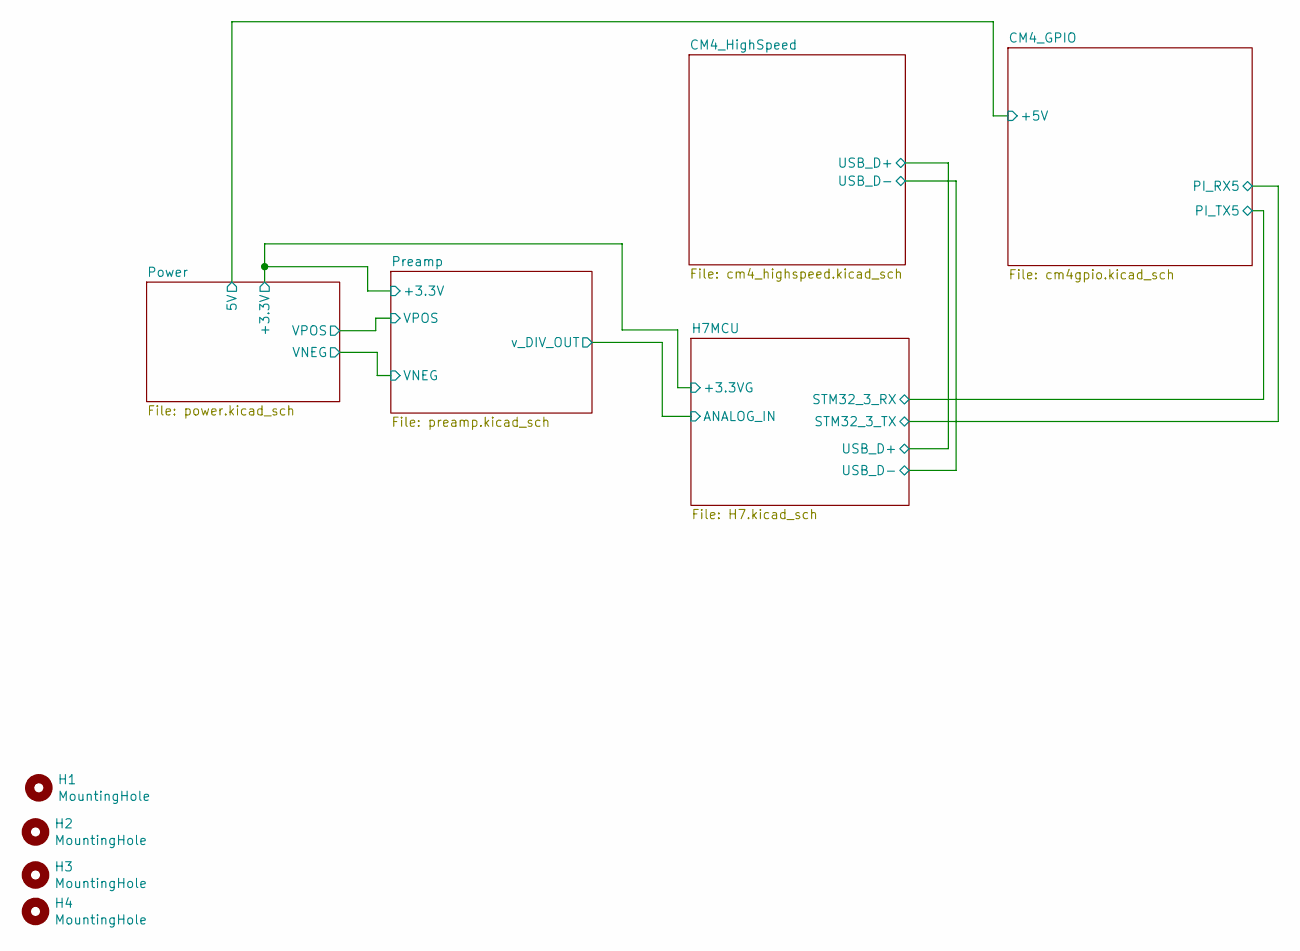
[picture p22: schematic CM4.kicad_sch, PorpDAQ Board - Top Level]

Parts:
H1, H2, H3, H4: MountingHole; MountingHole_3.2mm_M3_ISO14580_Pad

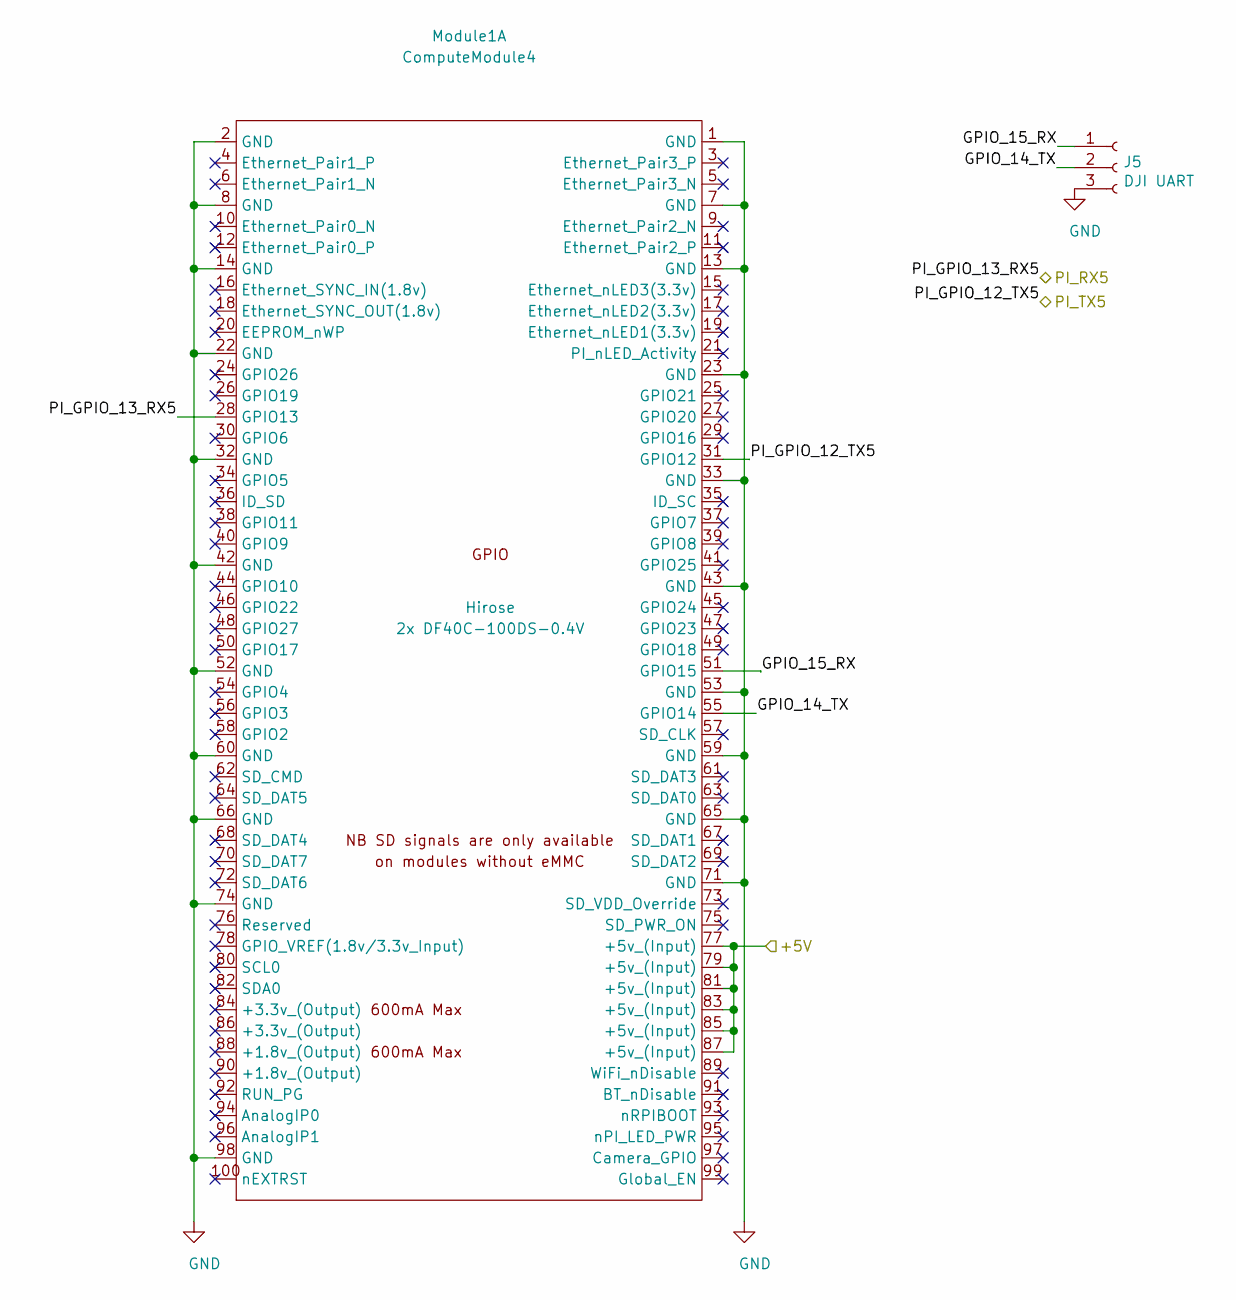
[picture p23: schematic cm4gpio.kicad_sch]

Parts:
J5: DJI UART; Molex_PicoBlade_53261-0371_1x03-1MP_P1.25mm_Horizontal
Module1: ComputeModule4; Raspberry-Pi-4-Compute-Module; Digi-Key_PN 2x H11615CT-ND

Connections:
/5V: Module1.77 (+5v_(Input)), Module1.79 (+5v_(Input)), Module1.81 (+5v_(Input)), Module1.83 (+5v_(Input)), Module1.85 (+5v_(Input)), Module1.87 (+5v_(Input)); also elsewhere on the board
/CM4_GPIO/GPIO_14_TX: J5.2, Module1.55 (GPIO14)
/CM4_GPIO/GPIO_15_RX: J5.1, Module1.51 (GPIO15)
/STM32_3_RX: Module1.31 (GPIO12); also elsewhere on the board
/STM32_3_TX: Module1.28 (GPIO13); also elsewhere on the board
GND: J5.3, Module1.1 (GND), Module1.2 (GND), Module1.7 (GND), Module1.8 (GND), Module1.13 (GND), Module1.14 (GND), Module1.22 (GND), Module1.23 (GND), Module1.32 (GND), Module1.33 (GND), Module1.42 (GND), Module1.43 (GND), Module1.52 (GND), Module1.53 (GND), Module1.59 (GND), Module1.60 (GND), Module1.65 (GND), Module1.66 (GND), Module1.71 (GND), Module1.74 (GND), Module1.98 (GND); also elsewhere on the board

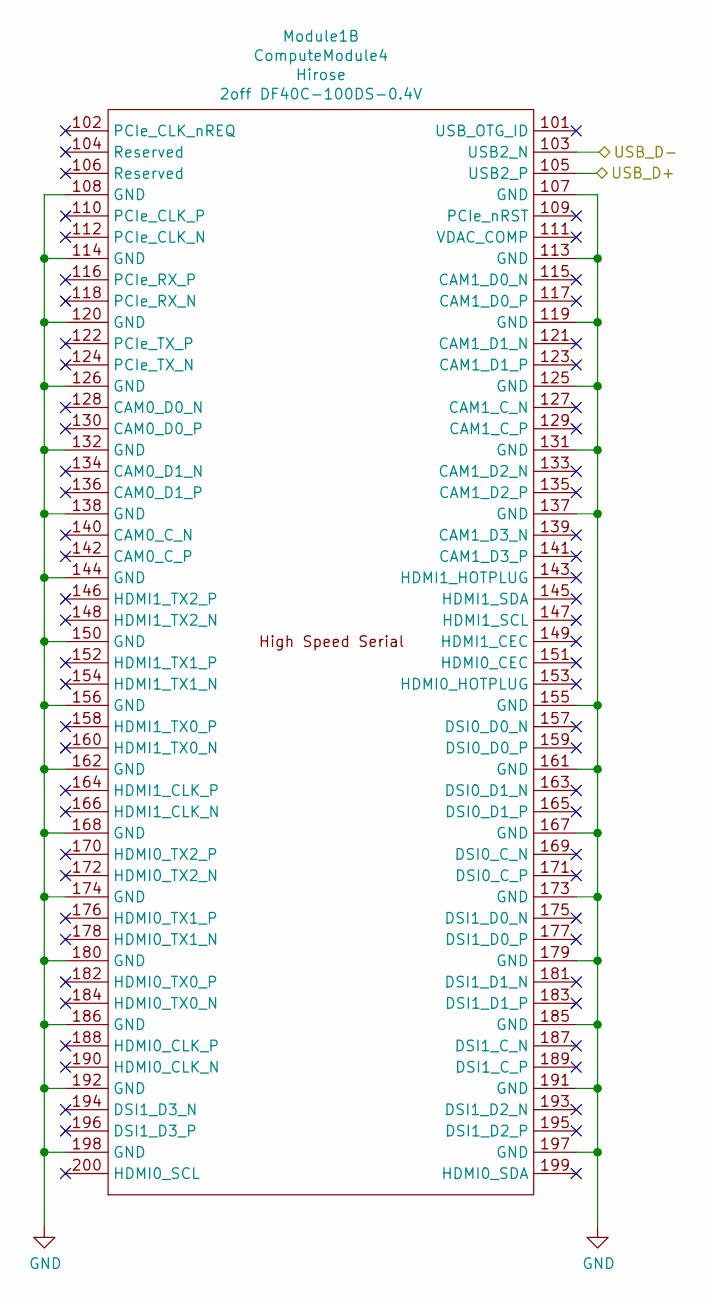
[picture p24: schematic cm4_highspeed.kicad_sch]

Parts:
Module1: ComputeModule4; Raspberry-Pi-4-Compute-Module; Part Description 100 Position Connector Receptacle, Cent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

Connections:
/USB_D+: Module1.105 (USB2_P); also elsewhere on the board
/USB_D-: Module1.103 (USB2_N); also elsewhere on the board
GND: Module1.107 (GND), Module1.108 (GND), Module1.113 (GND), Module1.114 (GND), Module1.119 (GND), Module1.120 (GND), Module1.125 (GND), Module1.126 (GND), Module1.131 (GND), Module1.132 (GND), Module1.137 (GND), Module1.138 (GND), Module1.144 (GND), Module1.150 (GND), Module1.155 (GND), Module1.156 (GND), Module1.161 (GND), Module1.162 (GND), Module1.167 (GND), Module1.168 (GND), Module1.173 (GND), Module1.174 (GND), Module1.179 (GND), Module1.180 (GND), Module1.185 (GND), Module1.186 (GND), Module1.191 (GND), Module1.192 (GND), Module1.197 (GND), Module1.198 (GND); also elsewhere on the board

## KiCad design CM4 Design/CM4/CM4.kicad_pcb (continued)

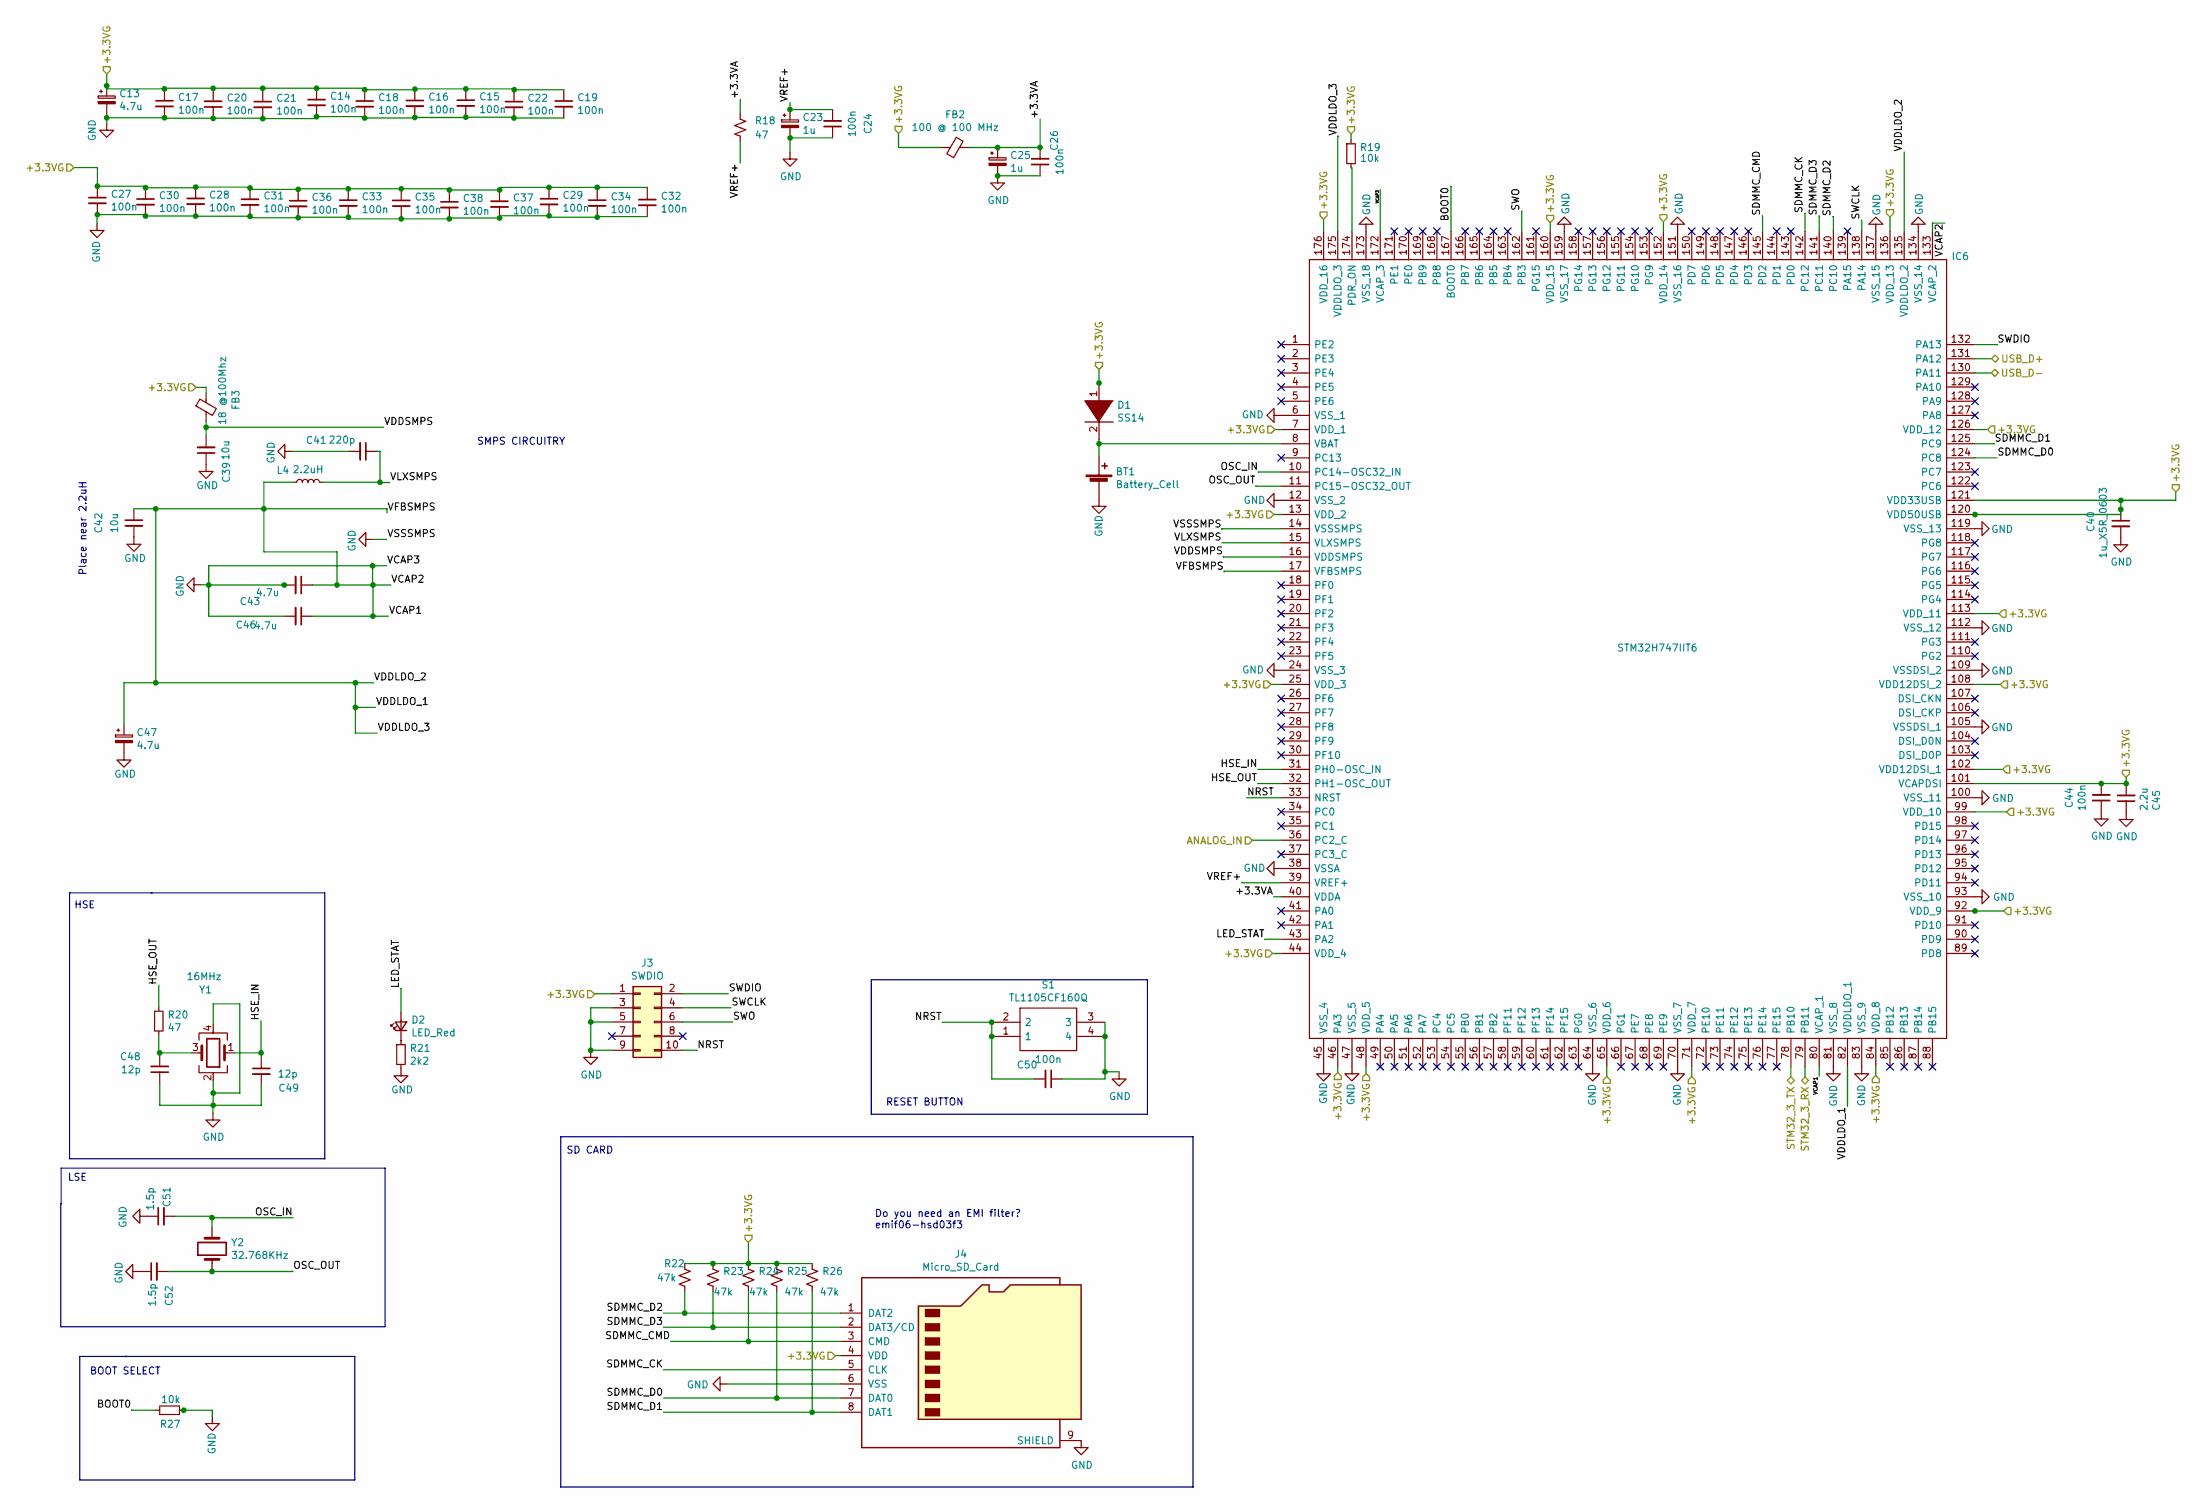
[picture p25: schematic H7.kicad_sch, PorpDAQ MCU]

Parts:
BT1: Battery_Cell; BatteryHolder_Keystone_3000_1x12mm
C13, C47: 4.7u; CP_EIA-3216-18_Kemet-A
C14, C15, C16, C17, C18, C19, C20, C21, C22, C24, C26, C27, C28, C29, C30, C31, C32, C33, C34, C35, C36, C37, C38, C44, C50: 100n; C_0402_1005Metric
C23, C25: 1u; CP_EIA-3216-18_Kemet-A
C39, C42: 10u; C_0402_1005Metric
C40: 1u_X5R_0603; C_0603_1608Metric
C41: 220p; C_0402_1005Metric
C43, C46: 4.7u; C_0402_1005Metric
C45: 2.2u; C_0603_1608Metric
C48, C49: 12p; C_0402_1005Metric
C51, C52: 1.5p; C_0402_1005Metric
D1: SS14; D_SMA
D2: LED_Red; LED_0603_1608Metric
FB2: 100 @ 100 MHz; L_0603_1608Metric
FB3: 18 @100Mhz; L_0603_1608Metric
IC6: STM32H747IIT6; QFP50P2600X2600X160-176N; Manufacturer_Part_Number STM32H747IIT6; Mouser Part Number 511-STM32H747IIT6
J3: SWDIO; PinHeader_2x05_P1.27mm_Vertical
J4: Micro_SD_Card; microSD_HC_Hirose_DM3AT-SF-PEJM5
L4: 2.2uH; L_0805_2012Metric
R18, R20: 47; R_0402_1005Metric
R19, R27: 10k; R_0402_1005Metric
R21: 2k2; R_0603_1608Metric
R22, R23, R24, R25, R26: 47k; R_0402_1005Metric
S1: TL1105CF160Q; Manufacturer_Part_Number TL1105CF160Q; Mouser Part Number 612-TL1105C
Y1: 16MHz; Crystal_SMD_3225-4Pin_3.2x2.5mm
Y2: 32.768KHz; Crystal_SMD_3215-2Pin_3.2x1.5mm

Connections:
/+3.3V: C13.1, C14.1, C15.1, C16.1, C17.1, C18.1, C19.1, C20.1, C21.1, C22.1, C27.1, C28.1, C29.1, C30.1, C31.1, C32.1, C33.1, C34.1, C35.1, C36.1, C37.1, C38.1, C40.1, C44.2, C45.2, D1.1 (K), FB2.1, FB3.1, IC6.7 (VDD_1), IC6.13 (VDD_2), IC6.25 (VDD_3), IC6.44 (VDD_4), IC6.46 (PA3), IC6.48 (VDD_5), IC6.65 (VDD_6), IC6.71 (VDD_7), IC6.84 (VDD_8), IC6.92 (VDD_9), IC6.99 (VDD_10), IC6.101 (VCAPDSI), IC6.102 (VDD12DSI_1), IC6.108 (VDD12DSI_2), IC6.113 (VDD_11), IC6.120 (VDD50USB), IC6.121 (VDD33USB), IC6.126 (VDD_12), IC6.136 (VDD_13), IC6.152 (VDD_14), IC6.160 (VDD_15), IC6.176 (VDD_16), J3.1, J4.4 (VDD), R19.1, R22.2, R23.2, R24.2, R25.2, R26.2; also elsewhere on the board
/H7MCU/+3.3VA: C25.1, C26.2, FB2.2, IC6.40 (VDDA), R18.2
/H7MCU/BOOT0: IC6.167 (BOOT0), R27.1
/H7MCU/HSE_IN: C49.1, IC6.31 (PH0-OSC_IN), Y1.1
/H7MCU/HSE_OUT: IC6.32 (PH1-OSC_OUT), R20.1
/H7MCU/LED_STAT: D2.2 (A), IC6.43 (PA2)
/H7MCU/NRST: C50.2, IC6.33 (NRST), J3.10, S1.1, S1.2
/H7MCU/OSC_IN: C51.2, IC6.10 (PC14-OSC32_IN), Y2.2
/H7MCU/OSC_OUT: C52.2, IC6.11 (PC15-OSC32_OUT), Y2.1
/H7MCU/SDMMC_CK: IC6.142 (PC12), J4.5 (CLK)
/H7MCU/SDMMC_CMD: IC6.145 (PD2), J4.3 (CMD), R24.1
/H7MCU/SDMMC_D0: IC6.124 (PC8), J4.7 (DAT0), R25.1
/H7MCU/SDMMC_D1: IC6.125 (PC9), J4.8 (DAT1), R26.1
/H7MCU/SDMMC_D2: IC6.140 (PC10), J4.1 (DAT2), R22.1
/H7MCU/SDMMC_D3: IC6.141 (PC11), J4.2 (DAT3/CD), R23.1
/H7MCU/SWCLK: IC6.138 (PA14), J3.4
/H7MCU/SWDIO: IC6.132 (PA13), J3.2
/H7MCU/SWO: IC6.162 (PB3), J3.6
/H7MCU/VCAP1: C42.1, C43.1, C46.1, C47.1, IC6.17 (VFBSMPS), IC6.80 (VCAP_1), IC6.82 (VDDLDO_1), IC6.133 (VCAP_2), IC6.135 (VDDLDO_2), IC6.175 (VDDLDO_3), L4.1
/H7MCU/VDDSMPS: C39.2, FB3.2, IC6.16 (VDDSMPS)
/H7MCU/VLXSMPS: C41.1, IC6.15 (VLXSMPS), L4.2
/H7MCU/VREF+: C23.1, C24.2, IC6.39 (VREF+), R18.1
/STM32_3_RX: IC6.79 (PB11); also elsewhere on the board
/STM32_3_TX: IC6.78 (PB10); also elsewhere on the board
/USB_D+: IC6.131 (PA12); also elsewhere on the board
/USB_D-: IC6.130 (PA11); also elsewhere on the board
/v_DIV_OUT: IC6.36 (PC2_C); also elsewhere on the board
GND: BT1.2 (-), C13.2, C14.2, C15.2, C16.2, C17.2, C18.2, C19.2, C20.2, C21.2, C22.2, C23.2, C24.1, C25.2, C26.1, C27.2, C28.2, C29.2, C30.2, C31.2, C32.2, C33.2, C34.2, C35.2, C36.2, C37.2, C38.2, C39.1, C40.2, C41.2, C42.2, C43.2, C44.1, C45.1, C46.2, C47.2, C50.1, C51.1, C52.1, IC6.6 (VSS_1), IC6.12 (VSS_2), IC6.14 (VSSSMPS), IC6.24 (VSS_3), IC6.38 (VSSA), IC6.45 (VSS_4), IC6.47 (VSS_5), IC6.64 (VSS_6), IC6.70 (VSS_7), IC6.81 (VSS_8), IC6.83 (VSS_9), IC6.93 (VSS_10), IC6.100 (VSS_11), IC6.105 (VSSDSI_1), IC6.109 (VSSDSI_2), IC6.112 (VSS_12), IC6.119 (VSS_13), IC6.134 (VSS_14), IC6.137 (VSS_15), IC6.151 (VSS_16), IC6.159 (VSS_17), IC6.172 (VCAP_3), IC6.173 (VSS_18), J3.3, J3.5, J3.9, J4.6 (VSS), J4.9 (SHIELD), R21.2, R27.2, S1.3, S1.4; also elsewhere on the board
unnamed: BT1.1 (+), D1.2 (A), IC6.8 (VBAT)
unnamed: C48.1, C49.2, Y1.2, Y1.4
unnamed: C48.2, R20.2, Y1.3
unnamed: D2.1 (K), R21.1
unnamed: IC6.174 (PDR_ON), R19.2

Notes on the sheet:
LSE
HSE
Place near 2.2uH
BOOT SELECT
SMPS CIRCUITRY
SD CARD
Do you need an EMI filter? emif06-hsd03f3
RESET BUTTON

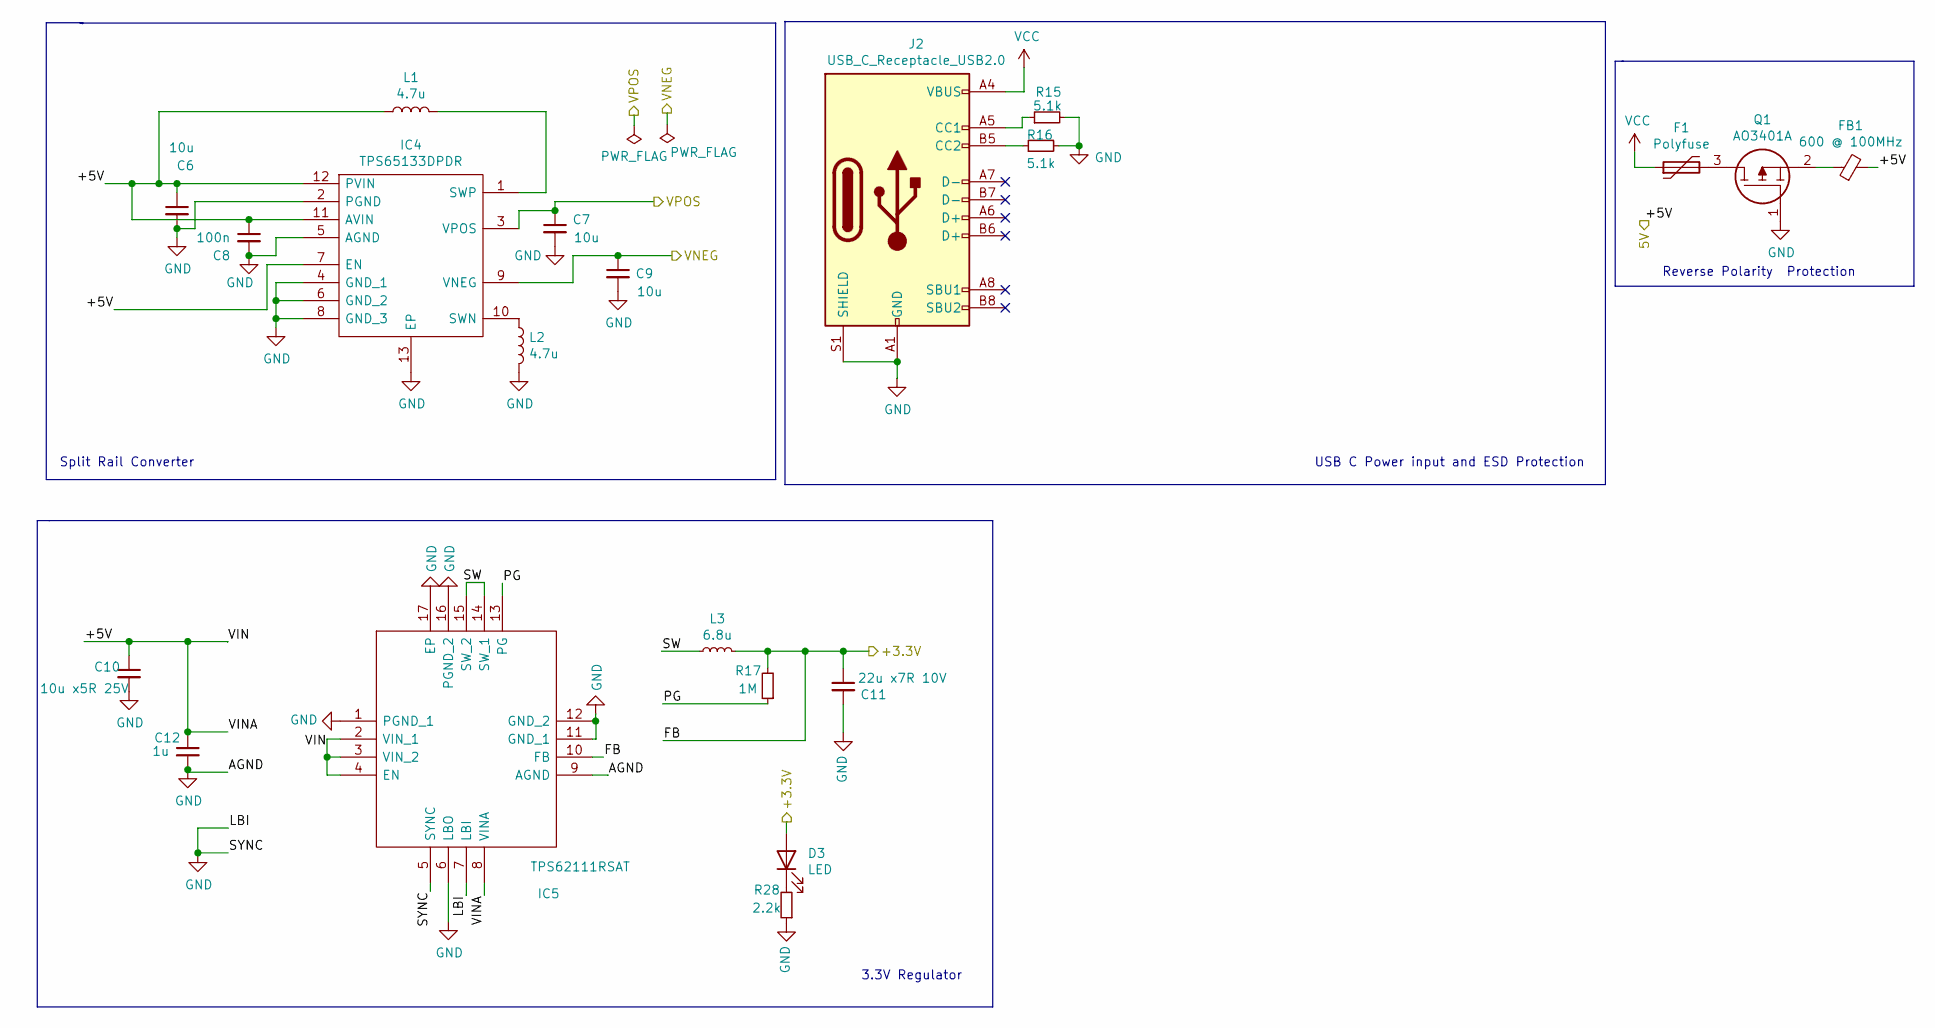
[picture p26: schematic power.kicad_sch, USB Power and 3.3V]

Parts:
C6, C7, C9: 10u; C_0805_2012Metric
C8: 100n; C_0805_2012Metric
C10: 10u x5R 25V; C_1210_3225Metric
C11: 22u x7R 10V; C_1210_3225Metric
C12: 1u; C_0805_2012Metric
D3: LED; LED_0603_1608Metric
F1: Polyfuse; Fuse_1206_3216Metric
FB1: 600 @ 100MHz; L_0805_2012Metric
IC4: TPS65133DPDR; SON45P300X300X80-13N-D; Manufacturer_Part_Number TPS65133DPDR; Mouser Part Number 595-TPS65133DPDR
IC5: TPS62111RSAT; QFN65P400X400X100-17N-D; Manufacturer_Part_Number TPS62111RSAT; Mouser Part Number 595-TPS62111RSAT
J2: USB_C_Receptacle_USB2.0; TYPE-C-31-M-12
L1, L2: 4.7u; L_Coilcraft_XxL4020
L3: 6.8u; L_TDK_SLF7032
Q1: AO3401A; SOT95P280X125-3N; Manufacturer_Part_Number AO3401A
R15, R16: 5.1k; R_1206_3216Metric
R17: 1M; R_0805_2012Metric
R28: 2.2k; R_0603_1608Metric

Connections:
/5V: C6.1, C8.1, C10.1, C12.1, FB1.2, IC4.7 (EN), IC4.11 (AVIN), IC4.12 (PVIN), IC5.2 (VIN_1), IC5.3 (VIN_2), IC5.4 (EN), IC5.8 (VINA), L1.1; also elsewhere on the board
/+3.3V: C11.1, D3.2 (A), IC5.10 (FB), L3.2, R17.2; also elsewhere on the board
/Power/PG: IC5.13 (PG), R17.1
/Power/SW: IC5.14 (SW_1), IC5.15 (SW_2), L3.1
/VNEG: C9.1, IC4.9 (VNEG); also elsewhere on the board
/VPOS: C7.1, IC4.3 (VPOS); also elsewhere on the board
GND: C6.2, C7.2, C8.2, C9.2, C10.2, C11.2, C12.2, IC4.2 (PGND), IC4.4 (GND_1), IC4.5 (AGND), IC4.6 (GND_2), IC4.8 (GND_3), IC4.13 (EP), IC5.1 (PGND_1), IC5.5 (SYNC), IC5.6 (LBO), IC5.7 (LBI), IC5.9 (AGND), IC5.11 (GND_1), IC5.12 (GND_2), IC5.16 (PGND_2), IC5.17 (EP), J2.A1 (GND), J2.A12 (GND), J2.B1 (GND), J2.B12 (GND), J2.S1 (SHIELD), L2.2, Q1.1, R15.2, R16.2, R28.1; also elsewhere on the board
unnamed: D3.1 (K), R28.2
unnamed: F1.2, Q1.3
unnamed: FB1.1, Q1.2
unnamed: IC4.1 (SWP), L1.2
unnamed: IC4.10 (SWN), L2.1
unnamed: J2.A5 (CC1), R15.1
unnamed: J2.B5 (CC2), R16.1
VCC: F1.1, J2.A4 (VBUS), J2.A9 (VBUS), J2.B4 (VBUS), J2.B9 (VBUS)

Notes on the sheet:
Split Rail Converter
3.3V Regulator
USB C Power input and ESD Protection
Reverse Polarity Protection

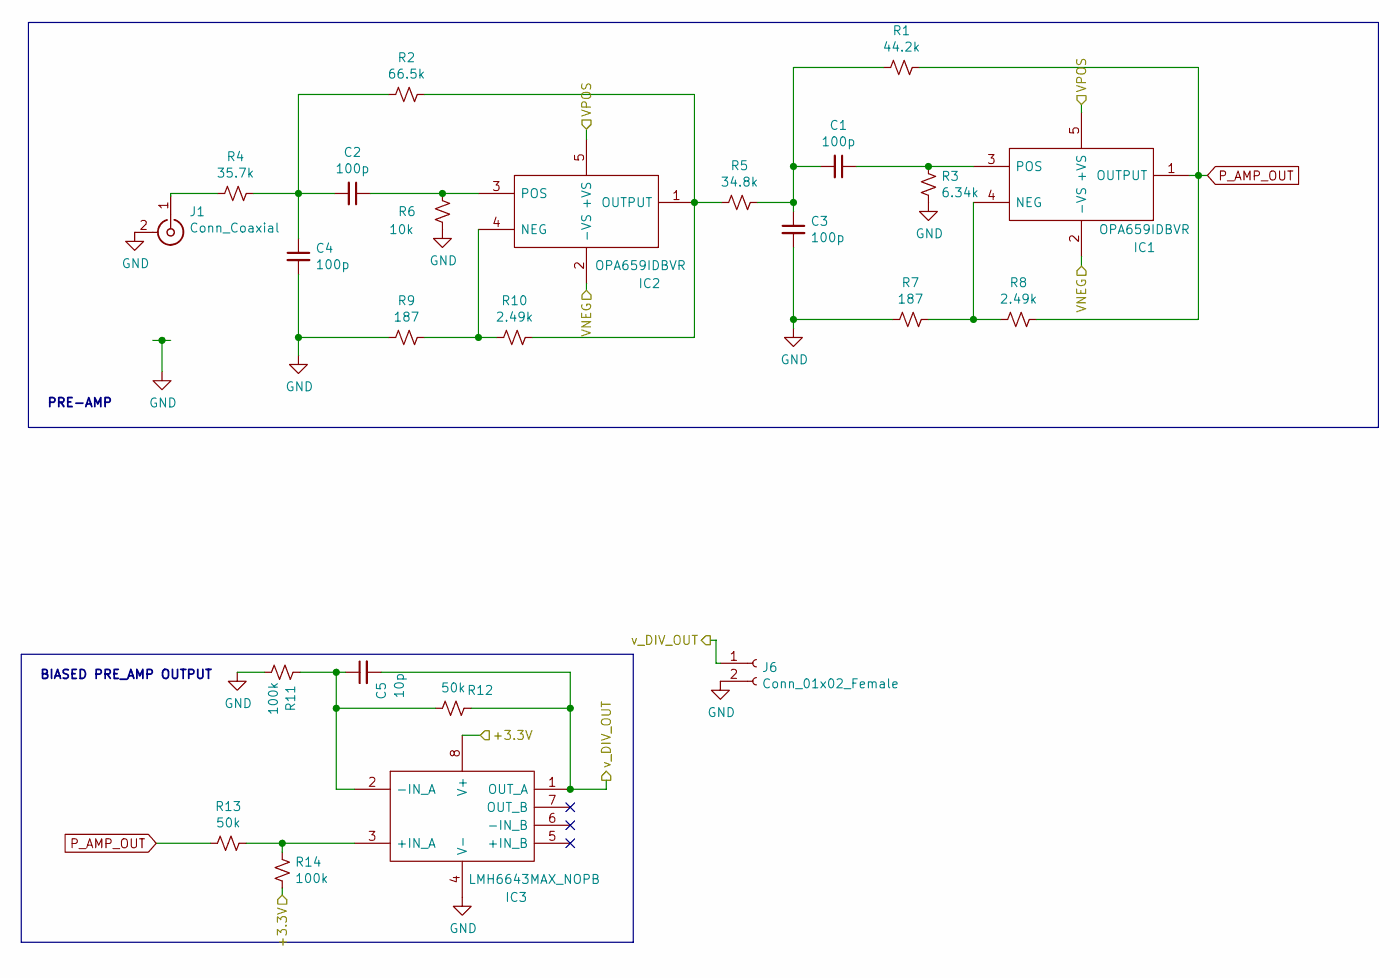
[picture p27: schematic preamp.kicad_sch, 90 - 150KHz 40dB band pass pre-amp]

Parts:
C1, C2, C3, C4: 100p; C_0402_1005Metric
C5: 10p; C_0402_1005Metric
IC1, IC2: OPA659IDBVR; SOT95P280X145-5N; Manufacturer_Part_Number OPA659IDBVR; Mouser Part Number 595-OPA659IDBVR
IC3: LMH6643MAX_NOPB; SOIC127P600X175-8N; Manufacturer_Part_Number LMH6643MAX/NOPB; Mouser Part Number 926-LMH6643MAX/NOPB
J1: Conn_Coaxial; SMA_Samtec_SMA-J-P-H-ST-EM1_EdgeMount
J6: Conn_01x02_Female; PinHeader_1x02_P2.54mm_Horizontal
R1: 44.2k; R_0402_1005Metric
R2: 66.5k; R_0402_1005Metric
R3: 6.34k; R_0402_1005Metric
R4: 35.7k; R_0402_1005Metric
R5: 34.8k; R_0402_1005Metric
R6: 10k; R_0402_1005Metric
R7, R9: 187; R_0402_1005Metric
R8, R10: 2.49k; R_0402_1005Metric
R11, R14: 100k; R_0603_1608Metric
R12, R13: 50k; R_0603_1608Metric

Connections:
/+3.3V: IC3.8 (V+), R14.1; also elsewhere on the board
/VNEG: IC1.2 (-VS), IC2.2 (-VS); also elsewhere on the board
/VPOS: IC1.5 (+VS), IC2.5 (+VS); also elsewhere on the board
/v_DIV_OUT: C5.2, IC3.1 (OUT_A), J6.1, R12.1; also elsewhere on the board
GND: C3.2, C4.2, IC3.4 (V-), J1.2 (Ext), J6.2, R3.1, R6.1, R7.2, R9.2, R11.1; also elsewhere on the board
unnamed: C1.1, IC1.3 (POS), R3.2
unnamed: C1.2, C3.1, R1.2, R5.1
unnamed: C2.1, IC2.3 (POS), R6.2
unnamed: C2.2, C4.1, R2.2, R4.1
unnamed: C5.1, IC3.2 (-IN_A), R11.2, R12.2
unnamed: IC1.4 (NEG), R7.1, R8.2
unnamed: IC2.1 (OUTPUT), R2.1, R5.2, R10.1
unnamed: IC2.4 (NEG), R9.1, R10.2
unnamed: IC3.3 (+IN_A), R13.1, R14.2
unnamed: J1.1 (In), R4.2
P_AMP_OUT: IC1.1 (OUTPUT), R1.1, R8.1, R13.2

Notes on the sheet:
BIASED PRE_AMP OUTPUT
PRE-AMP

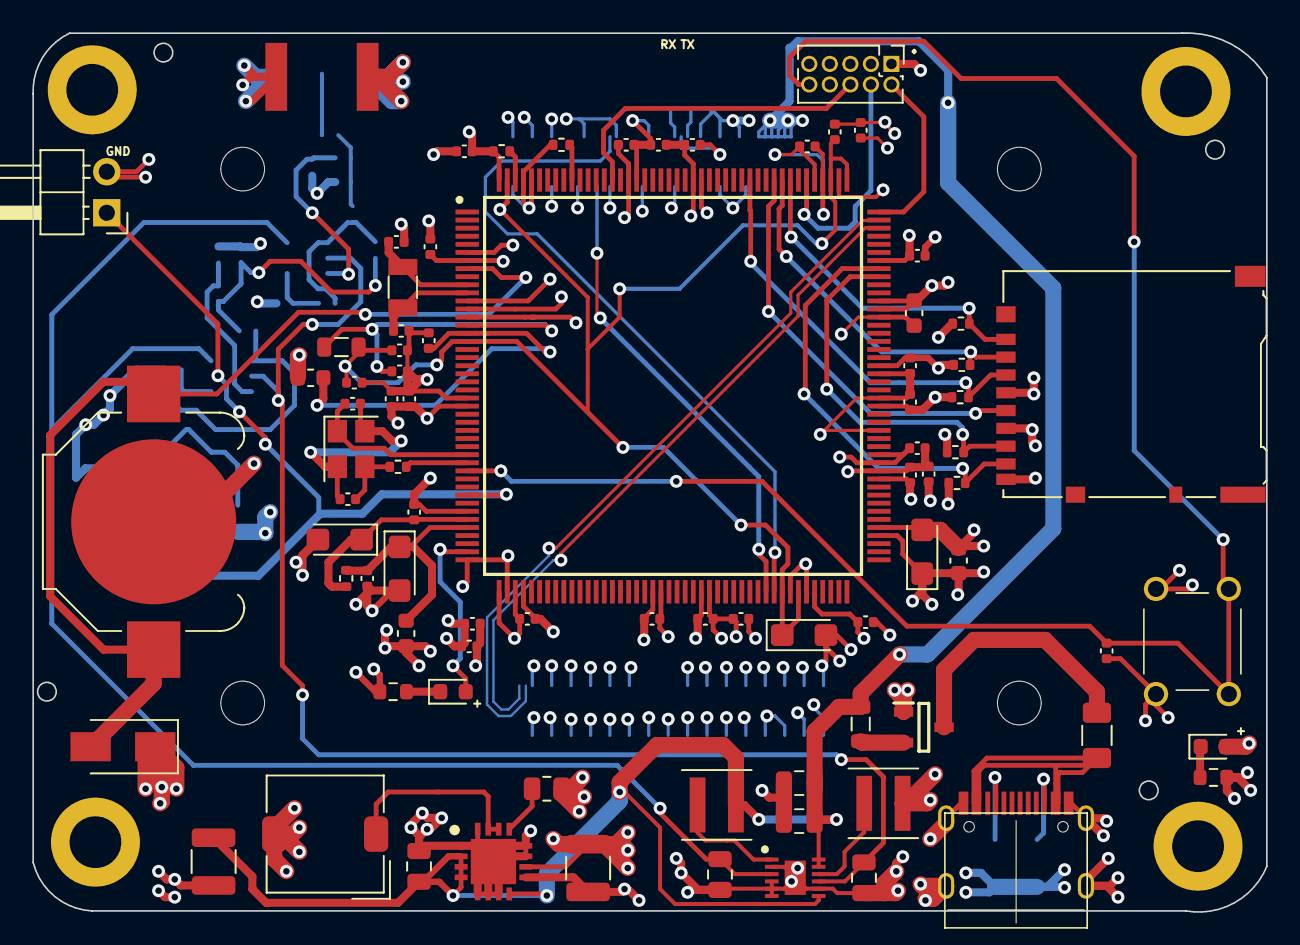
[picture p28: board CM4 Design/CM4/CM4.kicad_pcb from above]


Board: 4 copper layers, 76.2 x 54.3 mm, 113 parts (27 on the bottom side), 59 nets.

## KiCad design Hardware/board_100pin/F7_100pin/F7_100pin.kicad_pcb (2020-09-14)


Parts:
C1, C2: 2.2u; C_1206_3216Metric
C3, C4, C5, C6: 100p; C_0402_1005Metric
C7, C8: 4.3p; C_0402_1005Metric
C9: 10p; C_0402_1005Metric
C10, C11: 10u; C_0603_1608Metric
C12, C13, C15: 10u; C_0805_2012Metric
C14: 100n; C_0805_2012Metric
C16: 4.7u; CP_EIA-3216-18_Kemet-A
C17, C18, C19, C20, C21, C23, C25, C26: 100n; C_0402_1005Metric
C22, C24: 1u; CP_EIA-3216-18_Kemet-A
D1: B5819W; D_SOD-123
D2: Red_LED; LED_0603_1608Metric
D4: Green_LED; LED_0603_1608Metric
F1: 500mA; Fuse_0603_1608Metric
FB1: 100 @ 100 MHz; L_0603_1608Metric
FB2: 100 @ 100 Mhz; L_0603_1608Metric
H1: M_HolePad; MountingHole_3.2mm_M3_Pad_Via
H2, H3, H4: MHole_Pad; MountingHole_3.2mm_M3_Pad_Via
IC1, IC2: OPA659IDBVR; SOT95P280X145-5N; Manufacturer_Part_Number OPA659IDBVR; Mouser Part Number 595-OPA659IDBVR
IC3: LMH6643MAX_NOPB; SOIC127P600X175-8N; Manufacturer_Part_Number LMH6643MAX/NOPB; Mouser Part Number 926-LMH6643MAX/NOPB
IC4: TPS65133DPDR; SON45P300X300X80-13N-D; Manufacturer_Part_Number TPS65133DPDR; Mouser Part Number 595-TPS65133DPDR
J1: SMA Edge; 142-0701-851; Manufacturer_Part_Number 142-0701-851; Mouser Part Number 530-142-0701-851
J2: Pre-Amp; PinHeader_1x02_P2.54mm_Vertical
J3: UART; PinHeader_1x04_P2.54mm_Vertical
J4: USB_B_Micro; USB_Micro-B_GCT_USB3076-30-A
J5: Filter; PinHeader_1x02_P2.54mm_Vertical
J6: 3V3; PinHeader_1x02_P2.54mm_Vertical
J7: SWDIO; PinHeader_2x05_P1.27mm_Vertical
J8: Micro_SD_Card; microSD_HC_Hirose_DM3AT-SF-PEJM5
L1, L2: 4.7u; L_Coilcraft_XxL4020
R1: 44.2k; R_0402_1005Metric
R2: 66.5k; R_0402_1005Metric
R3: 35.7k; R_0402_1005Metric
R4: 34.8k; R_0402_1005Metric
R5: 6.34k; R_0402_1005Metric
R6, R13: 10k; R_0402_1005Metric
R7, R9: 187; R_0402_1005Metric
R8, R10: 2.49k; R_0402_1005Metric
R11, R15: 50k; R_0603_1608Metric
R12, R24: 2k2; R_0402_1005Metric
R14, R16: 100k; R_0603_1608Metric
R19, R20, R21, R22, R23: 47k; R_0402_1005Metric
R25: 0; R_0402_1005Metric
S1: TL1105CF160Q; Manufacturer_Part_Number TL1105CF160Q; Mouser Part Number 612-TL1105C
U1: AMS1117-3.3; SOT-223-3_TabPin2
U2: STM32F746VGTx; LQFP-100_14x14mm_P0.5mm
X1: NX3325GD; RESC3226X100N

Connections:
3V3: C11.1, C16.1, C17.2, C18.2, C19.2, C20.2, C21.2, D4.2 (A), FB2.1, IC3.8 (V+), J3.3, J6.1, J7.1, J8.4 (VDD), R14.1, R19.2, R20.2, R21.2, R22.2, R23.2, U1.2 (VO), U2.6 (VBAT), U2.11 (VDD), U2.27 (VDD), U2.50 (VDD), U2.75 (VDD), U2.100 (VDD)
3V3A: C24.1, C25.2, FB2.2, R25.2, U2.21 (VDDA)
BOOT0: R13.2, U2.94 (BOOT0)
GND: C1.2, C2.2, C5.2, C6.2, C7.2, C8.2, C10.2, C11.2, C12.2, C13.2, C14.2, C15.2, C16.2, C17.1, C18.1, C19.1, C20.1, C21.1, C22.2, C23.1, C24.2, C25.1, C26.1, H1.1, H2.1, H3.1, H4.1, IC3.4 (V-), IC4.2 (PGND), IC4.4 (GND_1), IC4.5 (AGND), IC4.6 (GND_2), IC4.8 (GND_3), IC4.13 (EP), J1.1, J1.3, J2.2, J3.4, J4.4 (ID), J4.5 (GND), J4.6 (Shield), J5.2, J6.2, J7.3, J7.5, J7.9, J8.6 (VSS), J8.9 (SHIELD), L2.2, R5.1, R6.1, R7.2, R9.2, R12.1, R13.1, R16.1, R24.1, S1.3, S1.4, U1.1 (GND), U2.10 (VSS), U2.19 (VSSA), U2.26 (VSS), U2.49 (VSS), U2.74 (VSS), U2.99 (VSS)
NRST: C26.2, J7.10, S1.1, S1.2, U2.14 (NRST)
unnamed: C1.1, U2.48 (VCAP_1)
unnamed: C2.1, U2.73 (VCAP_2)
unnamed: C3.1, IC1.3 (POS), R5.2
unnamed: C3.2, C5.1, R1.2, R4.1
unnamed: C4.1, IC2.3 (POS), R6.2
unnamed: C4.2, C6.1, R2.2, R3.1
unnamed: C7.1, U2.12 (PH0), X1.2
unnamed: C8.1, U2.13 (PH1), X1.1
unnamed: C9.1, IC3.2 (-IN_A), R11.2, R16.2
unnamed: C10.1, FB1.1, U1.3 (VI)
unnamed: D1.1 (K), F1.1
unnamed: D2.1 (K), R12.2
unnamed: D2.2 (A), U2.46 (PB10)
unnamed: D4.1 (K), R24.2
unnamed: F1.2, FB1.2
unnamed: IC1.4 (NEG), R7.1, R8.2
unnamed: IC2.1 (OUTPUT), R2.1, R4.2, R10.1
unnamed: IC2.4 (NEG), R9.1, R10.2
unnamed: IC3.3 (+IN_A), R14.2, R15.1
unnamed: IC4.1 (SWP), L1.2
unnamed: IC4.10 (SWN), L2.1
unnamed: J1.2, R3.2
P_AMP_OUT: IC1.1 (OUTPUT), J2.1, R1.1, R8.1, R15.2
SWCLK: J7.4, U2.76 (PA14)
SWDIO: J7.2, U2.72 (PA13)
SWO: J7.6, U2.89 (PB3)
USART_6_RX: J3.1, U2.64 (PC7)
USART_6_TX: J3.2, U2.63 (PC6)
VCC: C12.1, C14.1, D1.2 (A), IC4.7 (EN), IC4.11 (AVIN), IC4.12 (PVIN), J4.1 (VBUS), L1.1
VNEG: C15.1, IC1.2 (-VS), IC2.2 (-VS), IC4.9 (VNEG)
VPOS: C13.1, IC1.5 (+VS), IC2.5 (+VS), IC4.3 (VPOS)
VREF+: C22.1, C23.2, R25.1, U2.20 (VREF+)
uSD_CLK: J8.5 (CLK), U2.80 (PC12)
uSD_CMD: J8.3 (CMD), R21.1, U2.83 (PD2)
uSD_D0: J8.7 (DAT0), R22.1, U2.65 (PC8)
uSD_D1: J8.8 (DAT1), R23.1, U2.66 (PC9)
uSD_D2: J8.1 (DAT2), R19.1, U2.78 (PC10)
uSD_D3: J8.2 (DAT3/CD), R20.1, U2.79 (PC11)
v_DIV_OUT: C9.2, IC3.1 (OUT_A), J5.1, R11.1, U2.25 (PA3)

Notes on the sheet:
RESET BUTTON
Connectors
PWR_LED
PRE-AMP
Mounting Holes
INPUT VOLTAGE REGULATOR
SD CARD
BIASED PRE_AMP OUTPUT
USB-POWER


Board: 4 copper layers, 69.8 x 45.7 mm, 77 parts (0 on the bottom side), 44 nets.

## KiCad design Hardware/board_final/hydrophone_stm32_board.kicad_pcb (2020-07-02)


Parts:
C1, C3: 4.3p; C_0402_1005Metric
C2: 4.7u; CP_EIA-3216-18_Kemet-A
C4, C5, C6, C7, C8, C9, C10, C11, C12, C13, C14, C15, C16, C17, C18, C19, C20, C21, C22, C23, C24, C25, C26, C27, C35, C37, C41: 100n; C_0402_1005Metric
C30, C33: 2.2u; C_1206_3216Metric
C31, C32, C38, C40: 10u; C_0603_1608Metric
C34, C36: 1u; CP_EIA-3216-18_Kemet-A
C39: 100n; C_0603_1608Metric
C42, C46: 1.3n; C_0603_1608Metric
C43, C47: 1.1n; C_0603_1608Metric
C44, C48: 1.5n; C_0603_1608Metric
C45, C49: 1n; C_0603_1608Metric
D1: Green LED; LED_0603_1608Metric
D2: B5819W; D_SOD-123
D3: Red LED; LED_0603_1608Metric
F1: 500mA; Fuse_0603_1608Metric
FB1, FB2: 100 @ 100 MHz; L_0603_1608Metric
H1, H2, H3, H4: MountingHole_Pad; MountingHole_3.2mm_M3_Pad_Via
IC1: AD8031ARZ; SOIC127P600X175-8N; Manufacturer_Part_Number AD8031ARZ; Mouser Part Number 584-AD8031ARZ
J1, J3: Conn_01x02; PinHeader_1x02_P2.54mm_Vertical
J2: Conn_02x05_Odd_Even; PinHeader_2x05_P1.27mm_Vertical_SMD
J4: Conn_01x04; PinHeader_1x04_P2.54mm_Vertical
J5: Micro_SD_Card; microSD_HC_Hirose_DM3AT-SF-PEJM5
J6: 142-0701-851; Manufacturer_Part_Number 142-0701-851; Mouser Part Number 530-142-0701-851
J7: Conn_01x02_Female; PinHeader_1x02_P2.54mm_Vertical
R1: 2k2; R_0603_1608Metric
R2, R6, R7, R8, R9: 47k; R_0402_1005Metric
R3: 0; R_0402_1005Metric
R4, R5, R14, R15: 10k; R_0402_1005Metric
R11: 512; R_0603_1608Metric
R16: 4.99k; R_0402_1005Metric
R17: 4.52k; R_0402_1005Metric
R18: 4.39k; R_0402_1005Metric
R19: 11k; R_0402_1005Metric
R20: 10.4k; R_0402_1005Metric
R21: 418; R_0402_1005Metric
R22: 406; R_0402_1005Metric
R23: 1.02k; R_0402_1005Metric
R24: 966; R_0402_1005Metric
R25: 558; R_0402_1005Metric
R26: 541; R_0402_1005Metric
R27: 106; R_0402_1005Metric
R28: 100; R_0402_1005Metric
S1: TL1105CF160Q; Manufacturer_Part_Number TL1105CF160Q; Mouser Part Number 612-TL1105C
U1: AMS1117-3.3; SOT-223-3_TabPin2
U2: STM32F746ZGT6; LQFP-144_20x20mm_P0.5mm
U3, U4, U5, U6: ADA4807-1; SOT-23-6
Y1: Crystal; RESC3226X100N

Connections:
+3.3VA: C36.1, C37.1, FB2.1, R3.2, U2.33 (VDDA)
+3V3: C2.1, C4.1, C5.1, C6.1, C7.1, C8.1, C9.1, C10.1, C11.1, C12.1, C13.1, C14.1, C15.1, C16.1, C17.1, C18.1, C19.1, C20.1, C21.1, C22.1, C23.1, C24.1, C25.1, C26.1, C32.1, D1.2 (A), FB2.2, J2.1, J3.1, J4.3, J5.4 (VDD), R2.2, R5.2, R6.2, R7.2, R8.2, R9.2, R14.2, U1.2 (VO), U2.6 (VBAT), U2.17 (VDD), U2.30 (VDD), U2.39 (VDD), U2.52 (VDD), U2.62 (VDD), U2.72 (VDD), U2.84 (VDD), U2.95 (VDDUSB), U2.108 (VDD), U2.121 (VDD), U2.131 (VDD), U2.144 (VDD), U3.6 (V+), U4.6 (V+), U5.6 (V+), U6.6 (V+)
BOOT0: R4.2, U2.138 (BOOT0)
GND: C1.2, C2.2, C3.2, C4.2, C5.2, C6.2, C7.2, C8.2, C9.2, C10.2, C11.2, C12.2, C13.2, C14.2, C15.2, C16.2, C17.2, C18.2, C19.2, C20.2, C21.2, C22.2, C23.2, C24.2, C25.2, C26.2, C27.1, C30.2, C31.2, C32.2, C33.2, C34.2, C35.2, C36.2, C37.2, C38.1, C39.1, C40.1, C41.1, H1.1, H2.1, H3.1, H4.1, IC1.4 (-VS), J1.2, J2.3, J2.5, J2.9, J3.2, J4.4, J5.6 (VSS), J5.9 (SHIELD), J6.1, J6.3, J7.2, R1.2, R4.1, R11.1, R15.1, S1.2, S1.3, U1.1 (GND), U2.16 (VSS), U2.31 (VSSA), U2.38 (VSS), U2.51 (VSS), U2.61 (VSS), U2.83 (VSS), U2.94 (VSS), U2.107 (VSS), U2.120 (VSS), U2.130 (VSS), U3.2 (V-), U4.2 (V-), U5.2 (V-), U6.2 (V-)
NRST: C27.2, J2.10, S1.1, S1.4, U2.25 (NRST)
unnamed: C1.1, U2.23 (PH0), Y1.1
unnamed: C3.1, U2.24 (PH1), Y1.2
unnamed: C30.1, U2.71 (VCAP_1)
unnamed: C31.1, FB1.1, U1.3 (VI)
unnamed: C33.1, U2.106 (VCAP_2)
unnamed: C40.2, C41.2, IC1.3 (+IN), R14.1, R15.2
unnamed: C42.1, R17.2, R22.2, U3.1
unnamed: C42.2, C46.2, R21.1, R25.2
unnamed: C43.1, R18.2, R23.2, U4.1
unnamed: C43.2, C47.2, R22.1, R26.2
unnamed: C44.1, R19.2, R24.2, U5.1
unnamed: C44.2, C48.2, R23.1, R27.2
unnamed: C45.2, C49.2, R24.1, R28.2
unnamed: C46.1, R17.1, U3.4 (-)
unnamed: C47.1, R18.1, U4.4 (-)
unnamed: C48.1, R19.1, U5.4 (-)
unnamed: C49.1, R20.1, U6.4 (-)
unnamed: D1.1 (K), R1.1
unnamed: D2.1 (K), F1.1
unnamed: D3.1 (K), R11.2
unnamed: D3.2 (A), U2.69 (PB10)
unnamed: F1.2, FB1.2
unnamed: IC1.2 (-IN), R16.2
unnamed: J6.2, R21.2
PDR_ON: R5.1, U2.143 (PDR_ON)
SWCLK: J2.4, U2.109 (PA14)
SWDIO: J2.2, U2.105 (PA13)
SWO: J2.6, U2.133 (PB3)
USART6_RX: J4.2, U2.97 (PC7)
USART6_TX: J4.1, U2.96 (PC6)
VCC: D2.2 (A), J1.1
VDIV: C38.2, C39.2, IC1.6 (OUT), R16.1, R25.1, R26.1, R27.1, R28.1, U3.3 (+), U4.3 (+), U5.3 (+), U6.3 (+)
VREF+: C34.1, C35.1, R3.1, U2.32 (VREF+)
V_OUT: C45.1, J7.1, R20.2, U2.22 (PF10), U6.1
uSD_CLK: J5.5 (CLK), U2.113 (PC12)
uSD_CMD: J5.3 (CMD), R8.1, U2.116 (PD2)
uSD_D0: J5.7 (DAT0), R2.1, U2.98 (PC8)
uSD_D1: J5.8 (DAT1), R9.1, U2.99 (PC9)
uSD_D2: J5.1 (DAT2), R6.1, U2.111 (PC10)
uSD_D3: J5.2 (DAT3/CD), R7.1, U2.112 (PC11)

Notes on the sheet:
Input Voltage Regulator
RESET BUTTON
PREAMP VOLTAGE DIVIDER
PREAMP
PWR_LED
Connectors
MCU
Mounting Holes

Board: 4 copper layers, 98 parts (0 on the bottom side), 45 nets, no tracks yet.

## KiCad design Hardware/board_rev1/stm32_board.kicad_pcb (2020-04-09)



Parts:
C1, C3, C4, C5, C7, C8, C10, C11, C13, C14, C15, C16, C19, C20, C21, C23, C24, C25, C26, C27, C28, C29, C31, C34, C38, C52: 100n; C_0402_1005Metric
C2, C6: 4.7u; CP_EIA-3216-18_Kemet-A
C17, C22, C51: 1u; CP_EIA-3216-18_Kemet-A
C18, C33: 1u; C_0603_1608Metric
C30, C32: 2.2u; C_1206_3216Metric
C37, C43: 10u; C_0603_1608Metric
C39, C40: 4.7p; C_0402_1005Metric
C41, C42: 1.3n; C_0603_1608Metric
C44: 100n; C_0603_1608Metric
C45, C46: 1.1n; C_0603_1608Metric
C47, C48: 1.5n; C_0603_1608Metric
C49, C50: 1n; C_0603_1608Metric
D1, D2: LED; LED_0603_1608Metric
J1: USB_B_Micro; USB_Micro-B_Molex_47346-0001
J2: PJS008-2003-1; PJS00820031; Manufacturer_Part_Number PJS008-2003-1; Mouser Part Number 945-PJS008-2003-1
J3: 142-0701-851; Manufacturer_Part_Number 142-0701-851; Mouser Part Number 530-142-0701-851
J4: Conn_01x03_Female; PinHeader_1x03_P2.54mm_Vertical
J5: Conn_01x06_Male; PinHeader_1x06_P2.54mm_Vertical
J6: Conn_01x02_Female; PinHeader_1x02_P2.54mm_Vertical
L1: FCM1608KF-601T03; L_0603_1608Metric
PS1: LD39050PU33R; SON95P300X300X100-7N-D; Manufacturer_Part_Number LD39050PU33R; Mouser Part Number 511-LD39050PU33R
R1, R2, R3, R4, R5: 47k; R_0402_1005Metric
R6, R7, R11, R15, R17, R18, R21, R22: 10k; R_0402_1005Metric
R8, R13: 0; R_0402_1005Metric
R10, R16, R19: NA; R_0402_1005Metric
R12: 510; R_0402_1005Metric
R14, R39: 100; R_0402_1005Metric
R25: 4.99k; R_0402_1005Metric
R26: 418; R_0402_1005Metric
R27: 558; R_0402_1005Metric
R28: 4.52k; R_0402_1005Metric
R32: 406; R_0402_1005Metric
R33: 541; R_0402_1005Metric
R34: 4.39k; R_0402_1005Metric
R35: 1.02k; R_0402_1005Metric
R36: 106; R_0402_1005Metric
R37: 11k; R_0402_1005Metric
R38: 966; R_0402_1005Metric
R40: 10.4k; R_0402_1005Metric
S1: TL1105CF160Q; Manufacturer_Part_Number TL1105CF160Q; Mouser Part Number 612-TL1105C
U1: STM32F746IETx; LQFP-176_24x24mm_P0.5mm
U2: AD8031ARZ-REEL; SOIC127P600X175-8N
U3, U4, U5, U6: ADA4807-1; SOT-23-6
Y1: NZ2520SB-25.600MHZ; NZ2520SB25600MHZ; Manufacturer_Part_Number NZ2520SB-25.600MHZ; Mouser Part Number N/A
Y2: Crystal; Crystal_SMD_3215-2Pin_3.2x1.5mm

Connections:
3V3: C21.1, C33.2, C34.2, J2.4, J5.1, PS1.4 (VOUT), R1.2, R2.2, R3.2, R4.2, R5.2, R7.2, R10.2, R11.2, R15.2, R16.2, R21.2, U2.7 (+VS), U3.6 (V+), U4.6 (V+), U5.6 (V+), U6.6 (V+), Y1.4 (VCC); also elsewhere on the board
5V: C18.2, C24.2, J1.1 (VBUS), PS1.1 (EN), PS1.6 (VIN), R6.2
GND: C1.2, C2.2, C3.2, C4.2, C5.2, C6.2, C7.2, C8.2, C10.2, C11.2, C13.2, C14.2, C15.2, C16.2, C17.2, C18.1, C19.2, C20.2, C21.2, C22.2, C23.2, C24.1, C25.2, C26.2, C27.2, C28.2, C29.2, C30.1, C31.1, C32.1, C33.1, C34.1, C37.1, C38.1, C39.2, C40.1, C43.1, C44.1, C51.2, C52.2, D1.1 (K), D2.1 (K), J1.4 (ID), J1.5 (GND), J1.6 (Shield), J2.6, J2.SH1, J2.SH2, J2.SH3, J2.SH4, J2.SW2, J3.1, J3.3, J4.3, J5.3, J6.2, PS1.2 (GND), PS1.7 (PAD), R17.2, R18.2, R19.2, R22.1, S1.2, S1.3, U1.14 (VSS), U1.22 (VSS), U1.37 (VSSA), U1.61 (VSS), U1.71 (VSS), U1.90 (VSS), U1.102 (VSS), U1.113 (VSS), U1.126 (VSS), U1.135 (VSS), U1.148 (VSS), U1.158 (VSS), U2.4 (-VS), U3.2 (V-), U4.2 (V-), U5.2 (V-), U6.2 (V-), Y1.2 (GND)
NRST: C31.2, J5.5, R11.1, S1.1, S1.4, U1.31 (NRST)
unnamed: C30.2, U1.81 (VCAP_1)
unnamed: C32.2, U1.125 (VCAP_2)
unnamed: C37.2, C38.2, R21.1, R22.2, U2.3 (+IN)
unnamed: C39.1, U1.9 (PC14), Y2.1
unnamed: C40.2, U1.10 (PC15), Y2.2
unnamed: C41.1, R28.2, R32.2, U3.1
unnamed: C41.2, C42.2, R26.1, R27.2
unnamed: C42.1, R28.1, U3.4 (-)
unnamed: C45.1, R34.2, R35.2, U4.1
unnamed: C45.2, C46.2, R32.1, R33.2
unnamed: C46.1, R34.1, U4.4 (-)
unnamed: C47.1, R37.2, R38.2, U5.1
unnamed: C47.2, C48.2, R35.1, R36.2
unnamed: C48.1, R37.1, U5.4 (-)
unnamed: C49.2, C50.2, R38.1, R39.2
unnamed: C50.1, R40.1, U6.4 (-)
unnamed: D1.2 (A), R6.1
unnamed: D2.2 (A), R12.1
unnamed: J2.SW1, R8.2
unnamed: J3.2, R26.2
unnamed: R7.1, Y1.1 (STAND-BY)
unnamed: R12.2, U1.132 (PI1)
unnamed: R14.1, U1.29 (PH0)
unnamed: R14.2, Y1.3 (OUTPUT)
unnamed: R15.1, R19.1, U1.171 (PDR_ON)
unnamed: R16.1, R18.1, U1.166 (BOOT0)
unnamed: R17.1, U1.48 (BYPASS_REG)
unnamed: R25.2, U2.2 (-IN)
SWCLK: J5.2, U1.137 (PA14)
SWDIO: J5.4, U1.124 (PA13)
SWO: J5.6, U1.161 (PB3)
USART6_RX: J4.2, U1.116 (PC7)
USART6_TX: J4.1, U1.115 (PC6)
VDD: C1.1, C2.1, C3.1, C4.1, C5.1, C6.1, C7.1, C8.1, C10.1, C11.1, C13.1, C14.1, C15.1, C16.1, C17.1, C19.1, C20.1, C23.1, C25.1, C26.1, C27.1, C29.1, L1.2, U1.6 (VBAT), U1.15 (VDD), U1.23 (VDD), U1.36 (VDD), U1.49 (VDD), U1.62 (VDD), U1.72 (VDD), U1.82 (VDD), U1.91 (VDD), U1.103 (VDD), U1.114 (VDDUSB), U1.127 (VDD), U1.136 (VDD), U1.149 (VDD), U1.159 (VDD), U1.172 (VDD); also elsewhere on the board
VDDA: C22.1, C28.1, L1.1, R13.2, U1.39 (VDDA)
VREF: C43.2, C44.2, R25.1, R27.1, R33.1, R36.1, R39.1, U2.6 (OUT), U3.3 (+), U4.3 (+), U5.3 (+), U6.3 (+)
VREF+: C51.1, C52.1, R13.1, U1.38 (VREF+)
V_OUT: C49.1, J6.1, R40.2, U1.28 (PF10), U6.1
uSD_CLK: J2.5, U1.141 (PC12)
uSD_CMD: J2.3, R1.1, U1.144 (PD2)
uSD_D0: J2.7, R4.1, U1.117 (PC8)
uSD_D1: J2.8, R5.1, U1.118 (PC9)
uSD_D2: J2.1, R3.1, U1.139 (PC10)
uSD_D3: J2.2, R2.1, U1.140 (PC11)
uSD_Detect: R8.1, R10.1, U1.8 (PC13)

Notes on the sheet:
PREAMP VOLTAGE DIVIDER
PREAMP
VOLTAGE REGULATOR
USB_POWER
PWR_LED
uSD
RESET BUTTON
SWD


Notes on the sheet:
PREAMP VOLTAGE DIVIDER
uSD
PREAMP

Board: 2 copper layers, 101 parts (0 on the bottom side), 49 nets, no tracks yet.

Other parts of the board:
R20: 0; R_0402_1005Metric

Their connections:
3V3: R20.1; also elsewhere on the board
VDD: R20.2; also elsewhere on the board

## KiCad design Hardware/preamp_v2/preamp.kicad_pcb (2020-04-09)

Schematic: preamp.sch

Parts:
Battery1: Screw_Terminal_01x02; AMASS_XT30PW-M_1x02_P2.50mm_Horizontal
C1: 1uf; C_0603_1608Metric
C2: 220uF; CP_EIA-2012-15_AVX-P
C3, C4: 100nf; C_0603_1608Metric
C5, C6, C7, C8: 100pF; C_0603_1608Metric
C9: 10pF; C_0603_1608Metric
C10: 47uf; CP_EIA-2012-15_AVX-P
C11, C12, C13: 47uF; CP_EIA-2012-15_AVX-P
C14: 100nF; C_0603_1608Metric
J1: SMA-J-P-H-ST-EM1
J2, J3: Conn_01x02_Male; PinHeader_1x02_P1.00mm_Vertical
R1: 35.7k; R_0603_1608Metric
R2: 66.5k; R_0603_1608Metric
R3: 10k; R_0603_1608Metric
R4, R9: 187; R_0603_1608Metric
R5, R10: 2.49k; R_0603_1608Metric
R6: 34.8k; R_0603_1608Metric
R7: 44.2k; R_0603_1608Metric
R8: 6.34k; R_0603_1608Metric
R11, R14: 50k; R_0603_1608Metric
R12, R13: 100k; R_0603_1608Metric
R15: 330; R_0603_1608Metric
U1: TLE2426xD; SOIC-8_3.9x4.9mm_P1.27mm
U2, U3: OPA659IDBVR; SOT95P280X145-5N; Mouser Part Number 595-OPA659IDBVR
U4: LMH6643MA; SOIC127P600X175-8N
U5: LT1528CQ; DDPAK-5_Q

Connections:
B_SIG: C9.1, J3.1, R14.1, U4.1 (OUTA)
F_OUT: J2.1, R7.1, R10.1, R11.2, U3.1 (OUTPUT)
GND: C3.2, C4.2, C5.2, C8.2, C10.2, C11.2, C12.2, C13.2, C14.1, J1.2_1 (GND), J1.2_2 (GND), J1.3_1 (GND), J1.3_2 (GND), J2.2, J3.2, R3.1, R4.2, R8.1, R9.2, R13.2, R15.1, U1.1 (OUT), U4.4 (V-), U5.3 (GND_2), U5.6 (GND)
unnamed: C1.1, U1.8 (NOISE_REDUCTION)
unnamed: C5.1, C6.2, R1.1, R2.2
unnamed: C6.1, R3.2, U2.3 (POS)
unnamed: C7.1, R8.2, U3.3 (POS)
unnamed: C7.2, C8.1, R6.1, R7.2
unnamed: C9.2, R13.1, R14.2, U4.2 (-INA)
unnamed: C10.1, C11.1, C12.1, C13.1, C14.2, R12.2, R15.2, U4.8 (V+), U5.1 (OUTPUT), U5.2 (SENSE)
unnamed: J1.1 (SIGNAL), R1.2
unnamed: R2.1, R5.1, R6.2, U2.1 (OUTPUT)
unnamed: R4.1, R5.2, U2.4 (NEG)
unnamed: R9.1, R10.2, U3.4 (NEG)
unnamed: R11.1, R12.1, U4.3 (+INA)
V+: Battery1.2, C2.1, C3.1, U1.3 (IN), U2.5 (+VS), U3.5 (+VS), U5.5 (VIN)
V-: Battery1.1, C1.2, C2.2, C4.1, U1.2 (COMMON), U2.2 (-VS), U3.2 (-VS)


Board: 2 copper layers, 42 parts (0 on the bottom side), 17 nets.

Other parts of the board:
REF1, REF2, REF3, REF4: MountingHole_2.2mm_M2

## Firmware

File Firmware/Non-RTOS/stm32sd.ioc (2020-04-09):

#MicroXplorer Configuration settings - do not modify
ADC3.Channel-0\#ChannelRegularConversion=ADC_CHANNEL_8
ADC3.DMAContinuousRequests=ENABLE
ADC3.ExternalTrigConv=ADC_EXTERNALTRIGCONV_T1_TRGO
ADC3.ExternalTrigConvEdge=ADC_EXTERNALTRIGCONVEDGE_RISINGFALLING
ADC3.IPParameters=Rank-0\#ChannelRegularConversion,Channel-0\#ChannelRegularConversion,SamplingTime-0\#ChannelRegularConversion,NbrOfConversionFlag,DMAContinuousRequests,ExternalTrigConv,ExternalTrigConvEdge
ADC3.NbrOfConversionFlag=1
ADC3.Rank-0\#ChannelRegularConversion=1
ADC3.SamplingTime-0\#ChannelRegularConversion=ADC_SAMPLETIME_3CYCLES
CORTEX_M7.ART_ACCLERATOR_ENABLE=1
CORTEX_M7.CPU_DCache=Enabled
CORTEX_M7.CPU_ICache=Enabled
CORTEX_M7.IPParameters=ART_ACCLERATOR_ENABLE,PREFETCH_ENABLE,CPU_ICache,CPU_DCache
CORTEX_M7.PREFETCH_ENABLE=1
Dma.ADC3.2.Direction=DMA_PERIPH_TO_MEMORY
Dma.ADC3.2.FIFOMode=DMA_FIFOMODE_DISABLE
Dma.ADC3.2.Instance=DMA2_Stream0
Dma.ADC3.2.MemDataAlignment=DMA_MDATAALIGN_HALFWORD
Dma.ADC3.2.MemInc=DMA_MINC_ENABLE
Dma.ADC3.2.Mode=DMA_CIRCULAR
Dma.ADC3.2.PeriphDataAlignment=DMA_PDATAALIGN_HALFWORD
Dma.ADC3.2.PeriphInc=DMA_PINC_DISABLE
Dma.ADC3.2.Priority=DMA_PRIORITY_HIGH
Dma.ADC3.2.RequestParameters=Instance,Direction,PeriphInc,MemInc,PeriphDataAlignment,MemDataAlignment,Mode,Priority,FIFOMode
Dma.Request0=SDMMC1_RX
Dma.Request1=SDMMC1_TX
Dma.Request2=ADC3
Dma.Request3=UART7_RX
Dma.Request4=UART7_TX
Dma.RequestsNb=5
Dma.SDMMC1_RX.0.Direction=DMA_PERIPH_TO_MEMORY
Dma.SDMMC1_RX.0.FIFOMode=DMA_FIFOMODE_ENABLE
Dma.SDMMC1_RX.0.FIFOThreshold=DMA_FIFO_THRESHOLD_FULL
Dma.SDMMC1_RX.0.Instance=DMA2_Stream3
Dma.SDMMC1_RX.0.MemBurst=DMA_MBURST_INC4
Dma.SDMMC1_RX.0.MemDataAlignment=DMA_MDATAALIGN_WORD
Dma.SDMMC1_RX.0.MemInc=DMA_MINC_ENABLE
Dma.SDMMC1_RX.0.Mode=DMA_PFCTRL
Dma.SDMMC1_RX.0.PeriphBurst=DMA_PBURST_INC4
Dma.SDMMC1_RX.0.PeriphDataAlignment=DMA_PDATAALIGN_WORD
Dma.SDMMC1_RX.0.PeriphInc=DMA_PINC_DISABLE
Dma.SDMMC1_RX.0.Priority=DMA_PRIORITY_LOW
Dma.SDMMC1_RX.0.RequestParameters=Instance,Direction,PeriphInc,MemInc,PeriphDataAlignment,MemDataAlignment,Mode,Priority,FIFOMode,FIFOThreshold,MemBurst,PeriphBurst
Dma.SDMMC1_TX.1.Direction=DMA_MEMORY_TO_PERIPH
Dma.SDMMC1_TX.1.FIFOMode=DMA_FIFOMODE_ENABLE
Dma.SDMMC1_TX.1.FIFOThreshold=DMA_FIFO_THRESHOLD_FULL
Dma.SDMMC1_TX.1.Instance=DMA2_Stream6
Dma.SDMMC1_TX.1.MemBurst=DMA_MBURST_INC4
Dma.SDMMC1_TX.1.MemDataAlignment=DMA_MDATAALIGN_WORD
Dma.SDMMC1_TX.1.MemInc=DMA_MINC_ENABLE
Dma.SDMMC1_TX.1.Mode=DMA_PFCTRL
Dma.SDMMC1_TX.1.PeriphBurst=DMA_PBURST_INC4
Dma.SDMMC1_TX.1.PeriphDataAlignment=DMA_PDATAALIGN_WORD
Dma.SDMMC1_TX.1.PeriphInc=DMA_PINC_DISABLE
Dma.SDMMC1_TX.1.Priority=DMA_PRIORITY_LOW
Dma.SDMMC1_TX.1.RequestParameters=Instance,Direction,PeriphInc,MemInc,PeriphDataAlignment,MemDataAlignment,Mode,Priority,FIFOMode,FIFOThreshold,MemBurst,PeriphBurst
Dma.UART7_RX.3.Direction=DMA_PERIPH_TO_MEMORY
Dma.UART7_RX.3.FIFOMode=DMA_FIFOMODE_DISABLE
Dma.UART7_RX.3.Instance=DMA1_Stream3
Dma.UART7_RX.3.MemDataAlignment=DMA_MDATAALIGN_BYTE
Dma.UART7_RX.3.MemInc=DMA_MINC_ENABLE
Dma.UART7_RX.3.Mode=DMA_NORMAL
Dma.UART7_RX.3.PeriphDataAlignment=DMA_PDATAALIGN_BYTE
Dma.UART7_RX.3.PeriphInc=DMA_PINC_DISABLE
Dma.UART7_RX.3.Priority=DMA_PRIORITY_LOW
Dma.UART7_RX.3.RequestParameters=Instance,Direction,PeriphInc,MemInc,PeriphDataAlignment,MemDataAlignment,Mode,Priority,FIFOMode
Dma.UART7_TX.4.Direction=DMA_MEMORY_TO_PERIPH
Dma.UART7_TX.4.FIFOMode=DMA_FIFOMODE_DISABLE
Dma.UART7_TX.4.Instance=DMA1_Stream1
Dma.UART7_TX.4.MemDataAlignment=DMA_MDATAALIGN_BYTE
Dma.UART7_TX.4.MemInc=DMA_MINC_ENABLE
Dma.UART7_TX.4.Mode=DMA_NORMAL
Dma.UART7_TX.4.PeriphDataAlignment=DMA_PDATAALIGN_BYTE
Dma.UART7_TX.4.PeriphInc=DMA_PINC_DISABLE
Dma.UART7_TX.4.Priority=DMA_PRIORITY_HIGH
Dma.UART7_TX.4.RequestParameters=Instance,Direction,PeriphInc,MemInc,PeriphDataAlignment,MemDataAlignment,Mode,Priority,FIFOMode
File.Version=6
KeepUserPlacement=true
Mcu.Family=STM32F7
Mcu.IP0=ADC3
Mcu.IP1=CORTEX_M7
Mcu.IP2=DMA
Mcu.IP3=FATFS
Mcu.IP4=NVIC
Mcu.IP5=RCC
Mcu.IP6=SDMMC1
Mcu.IP7=SYS
Mcu.IP8=TIM1
Mcu.IP9=UART7
Mcu.IPNb=10
Mcu.Name=STM32F746NGHx
Mcu.Package=TFBGA216
Mcu.Pin0=PC12
Mcu.Pin1=PA14
Mcu.Pin10=PC8
Mcu.Pin11=PH1/OSC_OUT
Mcu.Pin12=PG6
Mcu.Pin13=PF7
Mcu.Pin14=PF6
Mcu.Pin15=PF10
Mcu.Pin16=VP_FATFS_VS_SDIO
Mcu.Pin17=VP_SYS_VS_Systick
Mcu.Pin18=VP_TIM1_VS_ClockSourceINT
Mcu.Pin2=PA13
Mcu.Pin3=PC11
Mcu.Pin4=PC10
Mcu.Pin5=PD2
Mcu.Pin6=PI1
Mcu.Pin7=PI11
Mcu.Pin8=PC9
Mcu.Pin9=PH0/OSC_IN
Mcu.PinsNb=19
Mcu.ThirdPartyNb=0
Mcu.UserConstants=
Mcu.UserName=STM32F746NGHx
MxCube.Version=5.4.0
MxDb.Version=DB.5.0.40
NVIC.ADC_IRQn=true\:0\:0\:false\:false\:true\:true\:true
NVIC.BusFault_IRQn=true\:0\:0\:false\:false\:true\:true\:false
NVIC.DMA1_Stream1_IRQn=true\:0\:0\:false\:false\:true\:false\:true
NVIC.DMA1_Stream3_IRQn=true\:0\:0\:false\:false\:true\:false\:true
NVIC.DMA2_Stream0_IRQn=true\:0\:0\:false\:false\:true\:false\:true
NVIC.DMA2_Stream3_IRQn=true\:0\:0\:false\:false\:true\:false\:true
NVIC.DMA2_Stream6_IRQn=true\:0\:0\:false\:false\:true\:false\:true
NVIC.DebugMonitor_IRQn=true\:0\:0\:false\:false\:true\:true\:false
NVIC.EXTI15_10_IRQn=true\:0\:0\:false\:false\:true\:true\:true
NVIC.ForceEnableDMAVector=true
NVIC.HardFault_IRQn=true\:0\:0\:false\:false\:true\:true\:false
NVIC.MemoryManagement_IRQn=true\:0\:0\:false\:false\:true\:true\:false
NVIC.NonMaskableInt_IRQn=true\:0\:0\:false\:false\:true\:true\:false
NVIC.PendSV_IRQn=true\:0\:0\:false\:false\:true\:true\:false
NVIC.PriorityGroup=NVIC_PRIORITYGROUP_4
NVIC.SDMMC1_IRQn=true\:0\:0\:false\:false\:true\:true\:true
NVIC.SVCall_IRQn=true\:0\:0\:false\:false\:true\:true\:false
NVIC.SysTick_IRQn=true\:0\:0\:false\:false\:true\:true\:true
NVIC.TIM1_BRK_TIM9_IRQn=true\:0\:0\:false\:false\:true\:true\:true
NVIC.TIM1_TRG_COM_TIM11_IRQn=true\:0\:0\:false\:false\:true\:true\:true
NVIC.TIM1_UP_TIM10_IRQn=true\:0\:0\:false\:false\:true\:true\:true
NVIC.UART7_IRQn=true\:0\:0\:false\:false\:true\:true\:true
NVIC.UsageFault_IRQn=true\:0\:0\:false\:false\:true\:true\:false
PA13.Mode=Serial_Wire
PA13.Signal=SYS_JTMS-SWDIO
PA14.Mode=Serial_Wire
PA14.Signal=SYS_JTCK-SWCLK
PC10.Mode=SD_4_bits_Wide_bus
PC10.Signal=SDMMC1_D2
PC11.Mode=SD_4_bits_Wide_bus
PC11.Signal=SDMMC1_D3
PC12.Mode=SD_4_bits_Wide_bus
PC12.Signal=SDMMC1_CK
PC8.Mode=SD_4_bits_Wide_bus
PC8.Signal=SDMMC1_D0
PC9.Mode=SD_4_bits_Wide_bus
PC9.Signal=SDMMC1_D1
PCC.Checker=false
PCC.Line=STM32F7x6
PCC.MCU=STM32F746NGHx
PCC.PartNumber=STM32F746NGHx
PCC.Seq0=0
PCC.Series=STM32F7
PCC.Temperature=25
PCC.Vdd=3.3
PD2.Mode=SD_4_bits_Wide_bus
PD2.Signal=SDMMC1_CMD
PF10.Mode=IN8
PF10.Signal=ADC3_IN8
PF6.Mode=Asynchronous
PF6.Signal=UART7_RX
PF7.Mode=Asynchronous
PF7.Signal=UART7_TX
PG6.Locked=true
PG6.Signal=GPIO_Output
PH0/OSC_IN.Mode=HSE-External-Oscillator
PH0/OSC_IN.Signal=RCC_OSC_IN
PH1/OSC_OUT.Mode=HSE-External-Oscillator
PH1/OSC_OUT.Signal=RCC_OSC_OUT
PI1.Locked=true
PI1.Signal=GPIO_Output
PI11.Locked=true
PI11.Signal=GPXTI11
PinOutPanel.CurrentBGAView=Top
PinOutPanel.RotationAngle=0
ProjectManager.AskForMigrate=true
ProjectManager.BackupPrevious=false
ProjectManager.CompilerOptimize=6
ProjectManager.ComputerToolchain=false
ProjectManager.CoupleFile=true
ProjectManager.CustomerFirmwarePackage=
ProjectManager.DefaultFWLocation=true
ProjectManager.DeletePrevious=true
ProjectManager.DeviceId=STM32F746NGHx
ProjectManager.FirmwarePackage=STM32Cube FW_F7 V1.15.0
ProjectManager.FreePins=false
ProjectManager.HalAssertFull=false
ProjectManager.HeapSize=0x2000
ProjectManager.KeepUserCode=true
ProjectManager.LastFirmware=true
ProjectManager.LibraryCopy=1
ProjectManager.MainLocation=Src
ProjectManager.NoMain=true
ProjectManager.PreviousToolchain=
ProjectManager.ProjectBuild=false
ProjectManager.ProjectFileName=stm32sd.ioc
ProjectManager.ProjectName=stm32sd
ProjectManager.StackSize=0x4000
ProjectManager.TargetToolchain=MDK-ARM V5
ProjectManager.ToolChainLocation=
ProjectManager.UnderRoot=false
ProjectManager.functionlistsort=1-MX_GPIO_Init-GPIO-false-HAL-true,2-MX_DMA_Init-DMA-false-HAL-true,3-SystemClock_Config-RCC-false-HAL-false,4-MX_SDMMC1_SD_Init-SDMMC1-false-HAL-true,5-MX_FATFS_Init-FATFS-false-HAL-false,6-MX_ADC3_Init-ADC3-false-HAL-true,7-MX_TIM1_Init-TIM1-false-HAL-true,8-MX_UART7_Init-UART7-false-HAL-true
RCC.AHBFreq_Value=216000000
RCC.APB1CLKDivider=RCC_HCLK_DIV4
RCC.APB1Freq_Value=54000000
RCC.APB1TimFreq_Value=108000000
RCC.APB2CLKDivider=RCC_HCLK_DIV2
RCC.APB2Freq_Value=108000000
RCC.APB2TimFreq_Value=216000000
RCC.CECFreq_Value=32786.88524590164
RCC.CortexFreq_Value=216000000
RCC.EthernetFreq_Value=216000000
RCC.FCLKCortexFreq_Value=216000000
RCC.FamilyName=M
RCC.HCLKFreq_Value=216000000
RCC.HSE_VALUE=25000000
RCC.HSI_VALUE=16000000
RCC.I2C1Freq_Value=54000000
RCC.I2C2Freq_Value=54000000
RCC.I2C3Freq_Value=54000000
RCC.I2C4Freq_Value=54000000
RCC.I2SFreq_Value=192000000
RCC.IPParameters=AHBFreq_Value,APB1CLKDivider,APB1Freq_Value,APB1TimFreq_Value,APB2CLKDivider,APB2Freq_Value,APB2TimFreq_Value,CECFreq_Value,CortexFreq_Value,EthernetFreq_Value,FCLKCortexFreq_Value,FamilyName,HCLKFreq_Value,HSE_VALUE,HSI_VALUE,I2C1Freq_Value,I2C2Freq_Value,I2C3Freq_Value,I2C4Freq_Value,I2SFreq_Value,LCDTFToutputFreq_Value,LPTIM1Freq_Value,LSE_VALUE,LSI_VALUE,MCO2PinFreq_Value,PLLCLKFreq_Value,PLLI2SPCLKFreq_Value,PLLI2SQCLKFreq_Value,PLLI2SRCLKFreq_Value,PLLI2SRoutputFreq_Value,PLLM,PLLN,PLLQ,PLLQCLKFreq_Value,PLLQoutputFreq_Value,PLLSAIPCLKFreq_Value,PLLSAIQCLKFreq_Value,PLLSAIRCLKFreq_Value,PLLSAIoutputFreq_Value,RNGFreq_Value,SAI1Freq_Value,SAI2Freq_Value,SDMMCClockSelection,SDMMCFreq_Value,SPDIFRXFreq_Value,SYSCLKFreq_VALUE,SYSCLKSource,UART4Freq_Value,UART5Freq_Value,UART7Freq_Value,UART8Freq_Value,USART1Freq_Value,USART2Freq_Value,USART3Freq_Value,USART6Freq_Value,USBFreq_Value,VCOI2SOutputFreq_Value,VCOInputFreq_Value,VCOOutputFreq_Value,VCOSAIOutputFreq_Value
RCC.LCDTFToutputFreq_Value=96000000
RCC.LPTIM1Freq_Value=54000000
RCC.LSE_VALUE=32768
RCC.LSI_VALUE=32000
RCC.MCO2PinFreq_Value=216000000
RCC.PLLCLKFreq_Value=216000000
RCC.PLLI2SPCLKFreq_Value=192000000
RCC.PLLI2SQCLKFreq_Value=192000000
RCC.PLLI2SRCLKFreq_Value=192000000
RCC.PLLI2SRoutputFreq_Value=192000000
RCC.PLLM=8
RCC.PLLN=216
RCC.PLLQ=9
RCC.PLLQCLKFreq_Value=48000000
RCC.PLLQoutputFreq_Value=48000000
RCC.PLLSAIPCLKFreq_Value=192000000
RCC.PLLSAIQCLKFreq_Value=192000000
RCC.PLLSAIRCLKFreq_Value=192000000
RCC.PLLSAIoutputFreq_Value=192000000
RCC.RNGFreq_Value=48000000
RCC.SAI1Freq_Value=192000000
RCC.SAI2Freq_Value=192000000
RCC.SDMMCClockSelection=RCC_SDMMC1CLKSOURCE_CLK48
RCC.SDMMCFreq_Value=48000000
RCC.SPDIFRXFreq_Value=192000000
RCC.SYSCLKFreq_VALUE=216000000
RCC.SYSCLKSource=RCC_SYSCLKSOURCE_PLLCLK
RCC.UART4Freq_Value=54000000
RCC.UART5Freq_Value=54000000
RCC.UART7Freq_Value=54000000
RCC.UART8Freq_Value=54000000
RCC.USART1Freq_Value=108000000
RCC.USART2Freq_Value=54000000
RCC.USART3Freq_Value=54000000
RCC.USART6Freq_Value=108000000
RCC.USBFreq_Value=48000000
RCC.VCOI2SOutputFreq_Value=384000000
RCC.VCOInputFreq_Value=2000000
RCC.VCOOutputFreq_Value=432000000
RCC.VCOSAIOutputFreq_Value=384000000
SDMMC1.ClockDiv=4
SDMMC1.IPParameters=ClockDiv
SH.GPXTI11.0=GPIO_EXTI11
SH.GPXTI11.ConfNb=1
TIM1.IPParameters=Period,TIM_MasterOutputTrigger,TIM_MasterOutputTrigger2
TIM1.Period=1080
TIM1.TIM_MasterOutputTrigger=TIM_TRGO_UPDATE
TIM1.TIM_MasterOutputTrigger2=TIM_TRGO2_UPDATE
VP_FATFS_VS_SDIO.Mode=SDIO
VP_FATFS_VS_SDIO.Signal=FATFS_VS_SDIO
VP_SYS_VS_Systick.Mode=SysTick
VP_SYS_VS_Systick.Signal=SYS_VS_Systick
VP_TIM1_VS_ClockSourceINT.Mode=Internal
VP_TIM1_VS_ClockSourceINT.Signal=TIM1_VS_ClockSourceINT
board=STM32F746G-DISCO
boardIOC=true

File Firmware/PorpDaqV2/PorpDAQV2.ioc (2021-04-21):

#MicroXplorer Configuration settings - do not modify
Mcu.Family=STM32H7
RCC.DIVQ2Freq_Value=75000000
ProjectManager.MainLocation=Core/Src
NVIC.ADC3_IRQn=true\:5\:0\:false\:false\:true\:true\:true\:true
Dma.ADC3.0.FIFOMode=DMA_FIFOMODE_DISABLE
VP_SYS_VS_tim6.Mode=TIM6
Dma.ADC3.0.Priority=DMA_PRIORITY_VERY_HIGH
RCC.SAI1Freq_Value=200000000
Dma.UART8_TX.2.PeriphDataAlignment=DMA_PDATAALIGN_BYTE
Dma.UART8_RX.1.MemInc=DMA_MINC_ENABLE
RCC.CortexFreq_Value=400000000
RCC.PLLDSIIDF=DSI_PLL_IN_DIV1
ProjectManager.KeepUserCode=true
Mcu.UserName=STM32H743VITx
Dma.UART8_RX.1.FIFOMode=DMA_FIFOMODE_DISABLE
RCC.HPRE=RCC_HCLK_DIV2
UART8.IPParameters=BaudRate
NVIC.TIM6_DAC_IRQn=true\:0\:0\:false\:false\:true\:false\:false\:true
VP_FATFS_VS_SDIO.Mode=SDIO
PH0-OSC_IN\ (PH0).Signal=RCC_OSC_IN
NVIC.DMA1_Stream2_IRQn=true\:5\:0\:false\:false\:true\:true\:false\:true
PC12.Signal=SDMMC1_CK
PC10.Signal=SDMMC1_D2
CORTEX_M7.TypeExtField-Cortex_Memory_Protection_Unit_Region0_Settings=MPU_TEX_LEVEL1
RCC.PLLFRACN=0
ProjectManager.functionlistsort=1-MX_GPIO_Init-GPIO-false-HAL-true,2-MX_DMA_Init-DMA-false-HAL-true,3-SystemClock_Config-RCC-false-HAL-false,4-MX_ADC3_Init-ADC3-false-HAL-true,5-MX_UART8_Init-UART8-false-HAL-true,6-MX_SDMMC1_SD_Init-SDMMC1-false-HAL-true,7-MX_TIM3_Init-TIM3-false-HAL-true,8-MX_FATFS_Init-FATFS-false-HAL-false,0-MX_CORTEX_M7_Init-CORTEX_M7-false-HAL-true
RCC.RTCFreq_Value=32000
SDMMC1.ClockDiv=2
Dma.UART8_RX.1.Priority=DMA_PRIORITY_HIGH
RCC.PLL2FRACN=3072
Dma.UART8_RX.1.RequestParameters=Instance,Direction,PeriphInc,MemInc,PeriphDataAlignment,MemDataAlignment,Mode,Priority,FIFOMode,SignalID,Polarity,RequestNumber,SyncSignalID,SyncPolarity,SyncEnable,EventEnable,SyncRequestNumber
RCC.CpuClockFreq_Value=400000000
RCC.VCO2OutputFreq_Value=150000000
Dma.UART8_TX.2.RequestNumber=1
ADC3.Channel-0\#ChannelRegularConversion=ADC_CHANNEL_0
PinOutPanel.RotationAngle=0
Dma.ADC3.0.SignalID=NONE
RCC.MCO1PinFreq_Value=64000000
RCC.SYSCLKSource=RCC_SYSCLKSOURCE_PLLCLK
ProjectManager.StackSize=0x400
Dma.ADC3.0.EventEnable=DISABLE
Dma.ADC3.0.SyncSignalID=NONE
RCC.AHB4Freq_Value=200000000
RCC.VCOInput3Freq_Value=500000
Dma.UART8_TX.2.PeriphInc=DMA_PINC_DISABLE
Dma.UART8_RX.1.EventEnable=DISABLE
RCC.LPTIM1Freq_Value=100000000
Mcu.IP4=FREERTOS
Mcu.IP5=NVIC
Mcu.IP2=DMA
NVIC.SVCall_IRQn=true\:0\:0\:false\:false\:false\:false\:false\:false
NVIC.SDMMC1_IRQn=true\:5\:0\:false\:false\:true\:true\:true\:true
Mcu.IP3=FATFS
Mcu.IP0=ADC3
Mcu.IP1=CORTEX_M7
CORTEX_M7.Enable-Cortex_Memory_Protection_Unit_Region0_Settings=MPU_REGION_ENABLE
Dma.UART8_RX.1.MemDataAlignment=DMA_MDATAALIGN_BYTE
Mcu.UserConstants=
VP_FATFS_VS_SDIO.Signal=FATFS_VS_SDIO
RCC.DIVP3Freq_Value=32250000
RCC.SDMMCFreq_Value=200000000
Mcu.ThirdPartyNb=0
RCC.HCLKFreq_Value=200000000
RCC.I2C4Freq_Value=100000000
Dma.UART8_TX.2.Mode=DMA_NORMAL
Mcu.IPNb=11
ProjectManager.PreviousToolchain=
Dma.UART8_TX.2.Polarity=HAL_DMAMUX_REQ_GEN_RISING
TIM3.Period=20-1
Dma.ADC3.0.Direction=DMA_PERIPH_TO_MEMORY
RCC.SPDIFRXFreq_Value=200000000
RCC.DIVQ3Freq_Value=32250000
Mcu.Pin6=PC10
Mcu.Pin7=PC11
Mcu.Pin8=PC12
Mcu.Pin9=PD2
Dma.UART8_TX.2.MemDataAlignment=DMA_MDATAALIGN_BYTE
PE1.Signal=UART8_TX
Dma.ADC3.0.MemDataAlignment=DMA_MDATAALIGN_HALFWORD
FREERTOS.IPParameters=Tasks01,configTOTAL_HEAP_SIZE,configMINIMAL_STACK_SIZE
FREERTOS.configMINIMAL_STACK_SIZE=12800
PC2_C.Signal=ADC3_INP0
Mcu.Pin0=PH0-OSC_IN (PH0)
Mcu.Pin1=PH1-OSC_OUT (PH1)
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

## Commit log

2020-04-09 Initial Commit.
    [AUDIO.SchDoc, Arduino_ Connectors.SchDoc, BOM.csv, BOM_JLC.csv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]
2020-07-02 Added F7 100 Pin Version
    [F7_100pin.kicad_pcb, F7_100pin.sch, hydrophone_stm32_board.kicad_pcb, hydrophone_stm32_board.sch]
2020-07-14 Added 100 pin version
    [F7_100pin-3V3.gbr, F7_100pin-B_Cu.gbr, F7_100pin-B_Mask.gbr, F7_100pin-B_Paste.gbr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]
2020-07-23 Updated F7 100 pin schematic
    [F7_100pin-3V3.gbr, F7_100pin-B_Cu.gbr, F7_100pin-B_Mask.gbr, F7_100pin-B_Paste.gbr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]
2020-09-14 Edited board to add USB power
    [BOM_JLC.csv, BOM_JLC.xlsx, F7_100pin (2).csv, F7_100pin-3V3.gbr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]
2020-09-14 Firmware added for custom board
2020-11-14 Changed naming scheme of WAV files
    [h7_rev.kicad_pcb, h7_rev.kicad_sch]
2020-11-19 Added initial H7 Design
    [CM4.kicad_pcb, CM4.kicad_sch, Case.STEP, DJI - A3 - GPS-Compass PRO.STEP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]
2020-11-24 Initial CM4IO board design
    [CM4.kicad_sch, F7_100pin.kicad_sch, H7.kicad_sch, cm4_highspeed.kicad_sch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]
2020-11-28 Completed H7/CM4IO Board
    [CM4.kicad_pcb, CM4.kicad_sch, H7.kicad_sch, cm4_highspeed.kicad_sch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]
2020-11-30 Corrected SMPS configuration
    [CM4-3V3.gbr, CM4-B_Cu.gbr, CM4-B_Mask.gbr, CM4-B_Paste.gbr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]
2021-01-26 Added H7 board hardware and firmware
    [CM4-3V3.gbr, CM4-BOM.csv, CM4-B_Cu.gbr, CM4-B_Mask.gbr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]
2021-02-24 Edited Design to modify to LDO regulator and improve board layout
    [CM4-B_Mask.gbr, CM4-B_Paste.gbr, CM4-B_Silkscreen.gbr, CM4-Edge_Cuts.gbr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]
2021-03-03 Added Low noise analysis and design files
    [CM4-3V3.gbr, CM4-BCu.gbr, CM4-BOM.csv, CM4-B_Cu.gbr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]
2021-04-21 Fixed HSE Clock Bug and changed target to LQFP100
    [CM4-3V3.gbr, CM4-BCu.gbr, CM4-BOM.csv, CM4-BOM.xlsx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]

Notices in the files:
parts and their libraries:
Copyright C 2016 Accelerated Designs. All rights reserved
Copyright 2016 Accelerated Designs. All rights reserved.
